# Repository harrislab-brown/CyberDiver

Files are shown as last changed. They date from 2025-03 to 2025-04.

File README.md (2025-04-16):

# CyberDiver: an untethered cyber-physical robotic impactor for water-entry experiments

<p align="center">
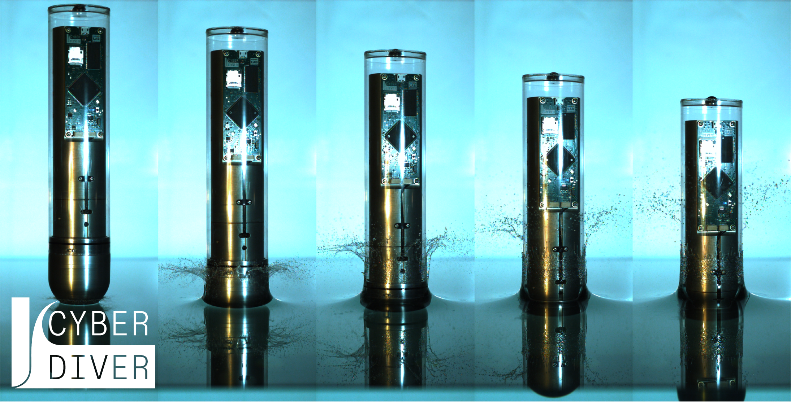
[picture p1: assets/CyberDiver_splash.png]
  
</p>

This repository provides design source files and raw data to complement the article ([https://arxiv.org/abs/2503.20702](https://arxiv.org/abs/2503.20702)). 

# License

CyberDiver is licensed under the CC BY-SA 4.0 Creative Commons license.

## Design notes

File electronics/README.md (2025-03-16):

# Electronics

This directory contains the KiCad design files, schematics, and Gerber files for the custom PCBs used in the CyberDiver. The control board and power board implement the majority of the functionality. The encoder daughterboard provides nose displacement measurements with an optical linear encoder (Celera CE300-40). The nose accelerometer board provides direct measurements of the impactor nose acceleration.

## Control board

<p align="center">
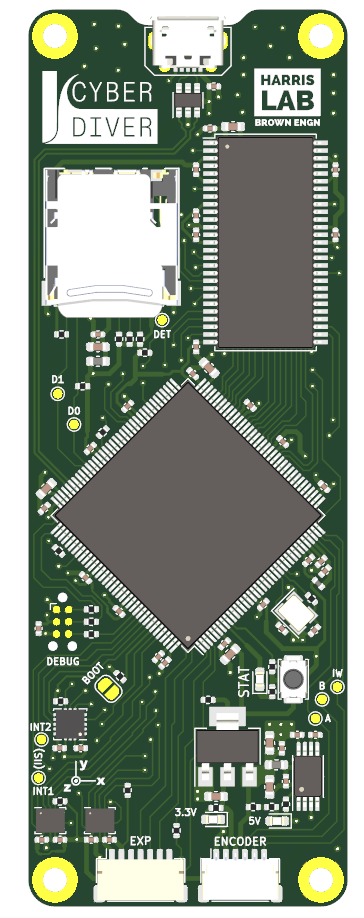
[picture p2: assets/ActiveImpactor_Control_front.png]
  
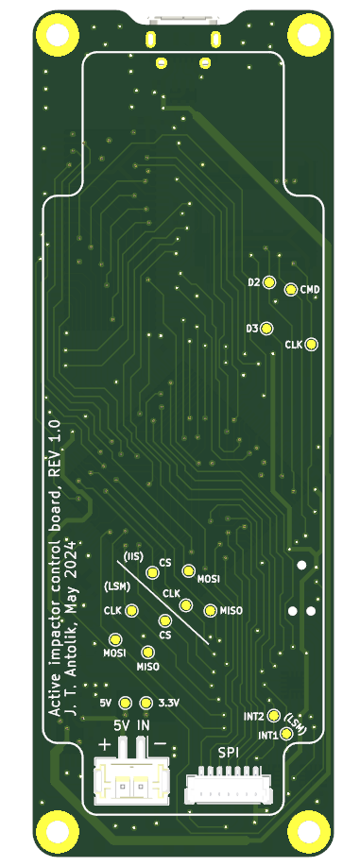
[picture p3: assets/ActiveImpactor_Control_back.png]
  
</p>

## Power board

<p align="center">
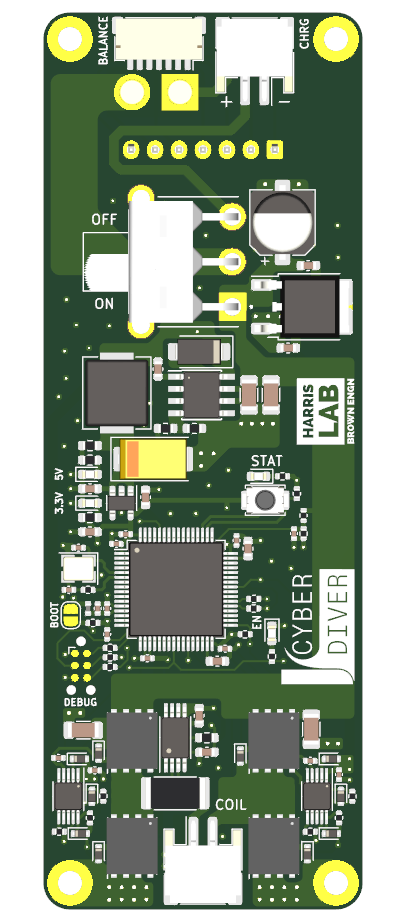
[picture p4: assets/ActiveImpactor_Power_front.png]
  
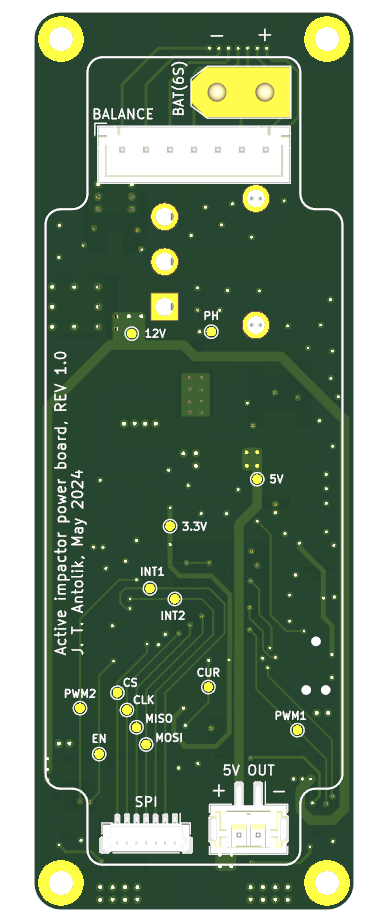
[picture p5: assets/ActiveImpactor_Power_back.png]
  
</p>

## Encoder daughter board

<p align="center">
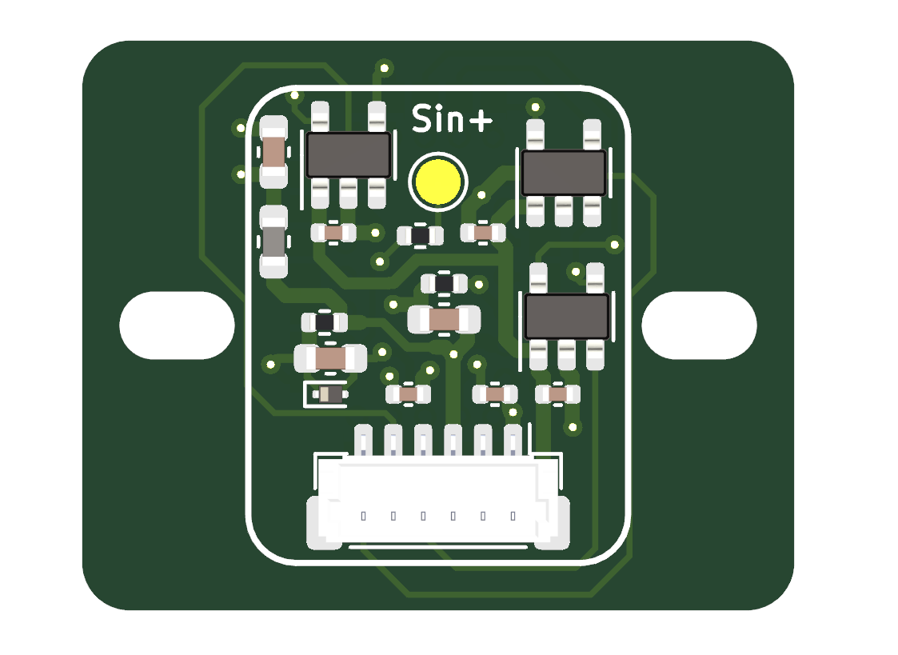
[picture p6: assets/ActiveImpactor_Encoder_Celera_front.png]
  
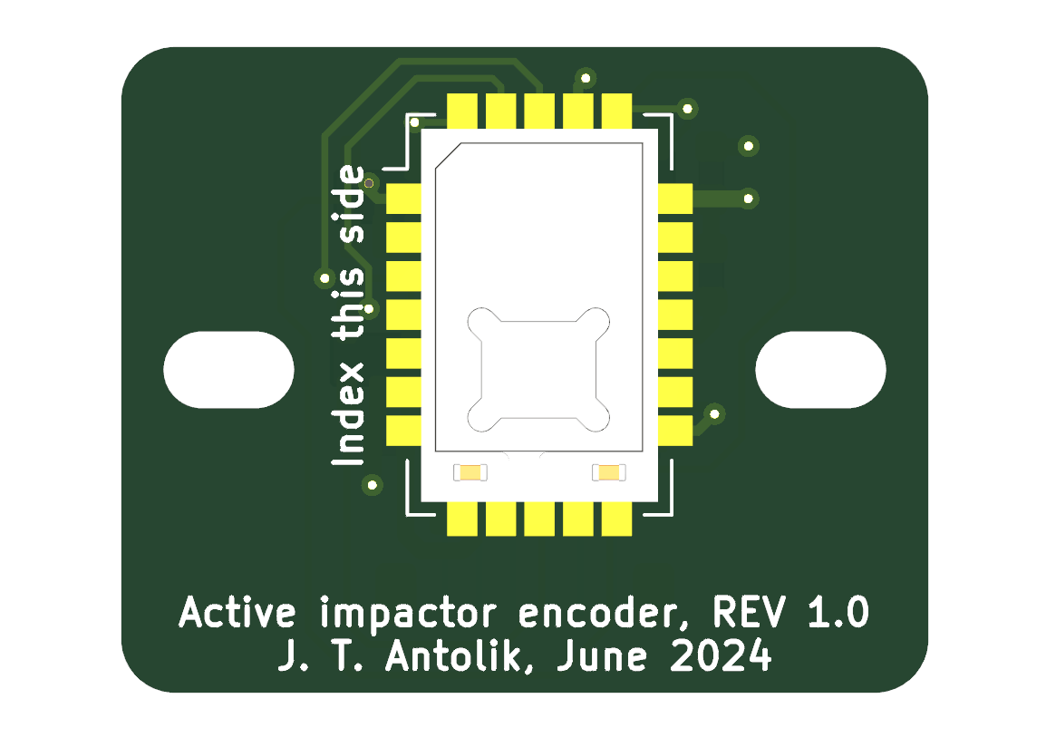
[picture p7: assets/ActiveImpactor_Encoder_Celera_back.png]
  
</p>

## Accelerometer daughter board

<p align="center">
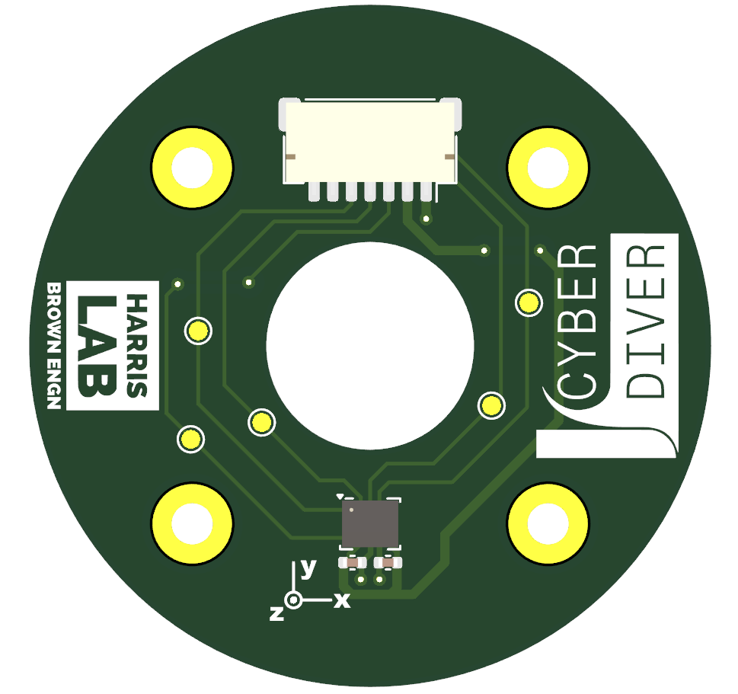
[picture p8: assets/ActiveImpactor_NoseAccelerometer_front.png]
  
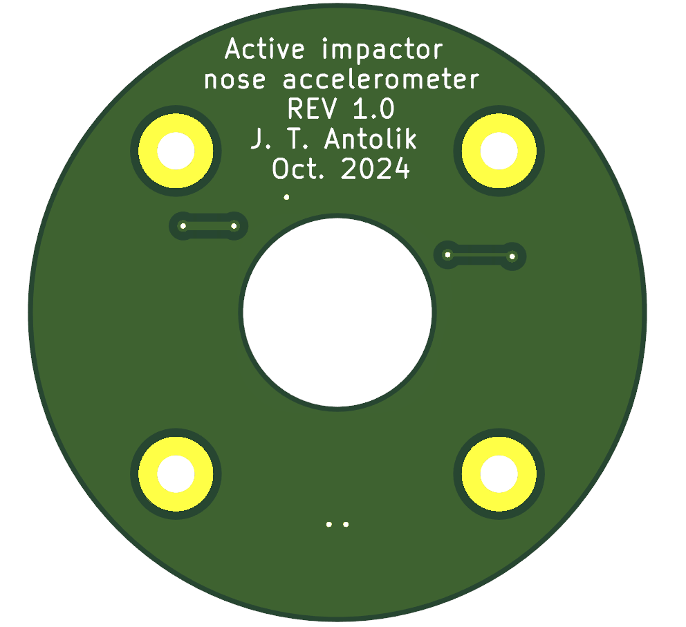
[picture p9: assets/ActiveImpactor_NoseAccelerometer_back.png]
  
</p>

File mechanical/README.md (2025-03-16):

# Mechanical

<p align="center">
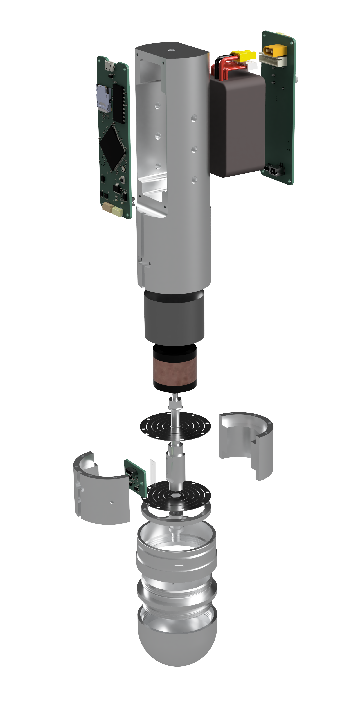
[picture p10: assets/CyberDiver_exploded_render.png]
  
</p>

This directory contains the mechanical design files for the CyberDiver including the native Autodesk Fusion 360 archive and step files. The disk flexures were laser-cut from blue-temper AISI 1075 spring steel sheet; everything else was machined from 6061 aluminum and clear anodized. The Python scripts can be executed with the Fusion 360 API to parametrically generate disk flexures with different cut profiles.

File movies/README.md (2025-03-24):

# Movies

This directory contains supplementary movies of the CyberDiver.

## Movie S1

CyberDiver entering the water at 4 m/s while behaving as a 5 N/mm undamped linear spring. The impact is filmed from above the water surface with front lighting to visualize the CyberDiver’s construction, corresponding to Figure 1(A) in the article. The playback is 100 times slower than actual speed.

## Movie S2

Demonstration of CyberDiver actuation and its position control operating mode. As the CyberDiver hangs from a bungee, a demonstration of its position control operating mode is initiated by pressing the button on the control board. The nose then moves relative to the body in a sinusoidal profile, illustrating the functionality of the actuator.

## Movie S3

Visualization of the impulse response of the cyber-physical system. An impulsive load is applied to the nose of the CyberDiver while it is suspended from a bungee and the vibrational response filmed. In the left frame, the cyber-physical system operates as a nominally undamped linear spring with 5 N/mm stiffness. In the right frame, the cyber-physical system operates as a nominally undamped linear spring with 15 N/mm stiffness. A corresponding visual difference between the amplitudes and frequencies of the vibrational responses is apparent. The playback is 25 times slower than actual speed.

## Movie S4

The CyberDiver manipulates the splash crown by performing active maneuvers during impact. The CyberDiver enters the water at 2 m/s and initiates an active maneuver at the moment of impact. Five different maneuver cases are shown where the impactor either extends or retracts the nose, resulting in amplification or attenuation of the splash formation, respectively. Movie version of Figures 6(A-E) in the article.

## Movie S5

Version of the CyberDiver splash manipulation movie with no labels. The playback in this video is 30 times slower than actual speed.

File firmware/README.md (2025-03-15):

# Firmware

This directory contains the STM32CubeIDE projects for the CyberDiver. The control board project specific header files can be found under firmware/CyberDiver_Control/Core/Inc and the implementation files under firmware/CyberDiver_Control/Core/Src. The power board project specific header files can be found under firmware/CyberDiver_Power/Core/Inc and the implementation files under firmware/CyberDiver_Power/Core/Src.

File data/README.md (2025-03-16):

# Data

<p align="center">
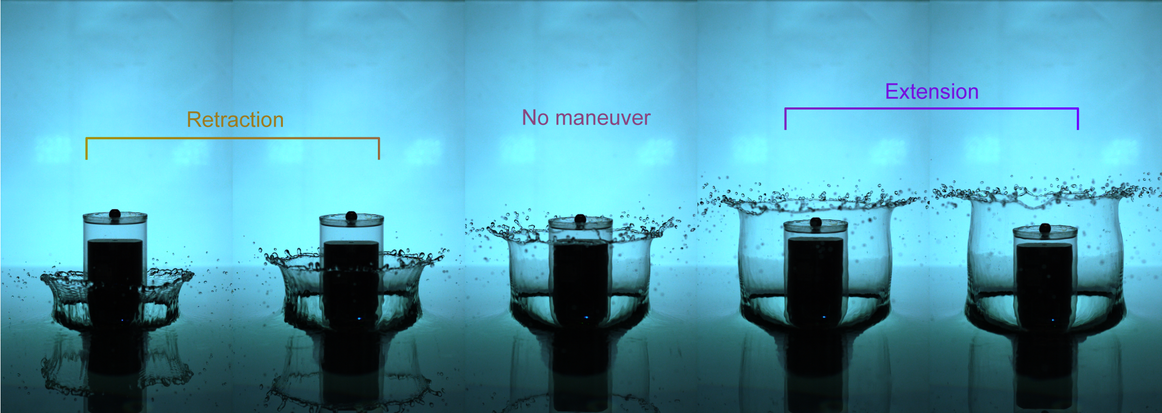
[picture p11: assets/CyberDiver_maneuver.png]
  
</p>

This directory contains the raw data files from our experiments using the CyberDiver. The CSV files contain aggregated tables of the peak acceleration corresponding to figures 3(D), 4(C), and 5(C).

## Validation

This directory contains the validation tests performed to confirm that the CyberDiver can behave as an undamped linear elastic cyber-physical system with programmable stifffess, corresponding to figures 3(A) and 3(B). The CSV files contain the quasi-static compression test results using a force test machine with displacements reported in mm and force in Newtons. The ".dat" files correspond to the dyamic ring down tests presented in figure 3(B). These are the binary data files produced by the CyberDiver that can be parsed using the provided MATLAB scripts. 

Additional force test machine results are provided for the nonlinear programmed  structural response corresponding to figure 5(A). Each of the compression test data files is labeled with either the programmed stiffness for the linear cases or the programmed force threshold in the nonlinear cases. 

Finally, ring down test data files corresponding to the damped cyber-physical structure in figure 4(A) are provided.

## Linear undamped

This directory contains the water entry experimental data files corresponding to figures 3(C) and 3(D). Each file is labeled with the linear programmed stiffness, the drop speed, and the trial number. These are the binary data files produced by the CyberDiver that can be parsed using the provided MATLAB functions in the scripts directory of this repository.

## Linear damped

This directory contains the water entry experimental data files corresponding to figures 4(B) and 4(C). Each file is labeled with the linear programmed stiffness, the drop speed, the programmed damping ratio, and the trial number. These are the binary data files produced by the CyberDiver that can be parsed using the provided MATLAB functions in the scripts directory of this repository.

## Nonlinear

This directory contains the water entry experimental data files corresponding to figures 5(B) and 5(C). Each file is labeled with the programmed force threshold, the drop speed, and the trial number. The stiffness of the linear region is 15 N/mm for all of the files in this folder. These are the binary data files produced by the CyberDiver that can be parsed using the provided MATLAB functions in the scripts directory of this repository.

## Splash manipulation

This directory contains the water entry data files corresponding to the active maneuver experiments in figure 6. Each file is labeled with the maneuver type and the trial number. These are the binary data files produced by the CyberDiver that can be parsed using the provided MATLAB functions in the scripts directory of this repository.

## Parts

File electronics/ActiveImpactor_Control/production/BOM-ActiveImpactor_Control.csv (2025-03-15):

Comment | Designator | Footprint | LCSC
100R | FB101,FB501 | L_0603_1608Metric | C1002
1k | R101,R102,R103,R104,R204 | R_0402_1005Metric | C11702
10n | C219 | C_0402_1005Metric | C15195
100n | C101,C102,C103,C105,C202,C204,C205,C207,C208,C209,C210,C211,C212,C213,C214,C215,C216,C217,C221,C301,C402,C403,C404,C405,C406,C407,C408,C501,C701,C702,C703,C704,C705,C706 | C_0402_1005Metric | C1525
12p | C203,C206 | C_0402_1005Metric | C1547
ENC | J601 | JST_SH_SM06B-SRSS-TB_1x06-1MP_P1.00mm_Horizontal | C160405
EXP | J801 | JST_SH_SM07B-SRSS-TB_1x07-1MP_P1.00mm_Horizontal | C160406
10u | C104,C201,C401,C502 | C_0603_1608Metric | C19702
DM3CS-SF | J501 | DM3CS-SF_HIR | C202111
BUTTON | SW201 | SW_Push_SPST_NO_Alps_SKRK | C202388
2u2 | C220,C222 | C_0603_1608Metric | C23630
22 | R205,R206,R207,R401,R502,R802 | R_0402_1005Metric | C25092
47 | R202 | R_0402_1005Metric | C25118
10k | R201,R203 | R_0402_1005Metric | C25744
47k | R501,R503,R504,R505,R506,R507,R701,R702,R703,R801 | R_0402_1005Metric | C25792
39n | L201 | L_0402_1005Metric | C26443
22u | C106,C107 | C_0603_1608Metric | C2762594
USBLC6-2SC6 | U301 | SOT-23-6 | C2827654
ADXL373 | U702 | Analog_LGA-16_3.25x3mm_P0.5mm_LayoutBorder3x5y | C3216386
USB_B_Micro | J301 | MicroXNJ | C404969
1u | C218 | C_0402_1005Metric | C52923
AMS1117-3.3 | U102 | SOT-223-3_TabPin2 | C6186
W9812G6KH-6 | U401 | TSOP-II-54_22.2x10.16mm_P0.8mm | C62379
TPS2115APWR | U101 | TSSOP-8_4.4x3mm_P0.65mm | C70287
24MHz | Y201 | Crystal_SMD_3225-4Pin_3.2x2.5mm | C70590
IIS3DWBTR | U703 | LGA-14_3x2.5mm_P0.5mm_LayoutBorder3x4y | C717702
STM32H723ZGTx | U201 | LQFP-144_20x20mm_P0.5mm | C730146
STAT | D201 | LED_0603_1608Metric | C84266
LED_5V | D101,D102 | LED_0603_1608Metric | C965805
LSM6DS3TR-C | U701 | LGA-14_3x2.5mm_P0.5mm_LayoutBorder3x4y | C967633

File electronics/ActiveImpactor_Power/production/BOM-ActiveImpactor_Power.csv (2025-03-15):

Comment | Designator | Footprint | LCSC
TLV70033_SOT23-5 | U102 | SOT-23-5 | C11337
1k | R109,R111,R201 | R_0402_1005Metric | C11702
100u | C101 | CP_Elec_6.3x5.8 | C128464
INA240A2PWR | U303 | TSSOP-8_4.4x3mm_P0.65mm | C129949
16MHz | Y201 | Crystal_SMD_3225-4Pin_3.2x2.5mm | C13738
7k5 | R108 | R_0402_1005Metric | C137934
100n | C303,C305 | C_0603_1608Metric | C14663
10n | C106,C210 | C_0402_1005Metric | C15195
100n | C202,C205,C206,C207,C208,C212 | C_0402_1005Metric | C1525
12p | C211,C213 | C_0402_1005Metric | C1547
STM32F405RGT6 | U201 | LQFP-64_10x10mm_P0.5mm | C15742
Balance | J104 | JST_SH_SM07B-SRSS-TB_1x07-1MP_P1.00mm_Horizontal | C160406
L7812 | U301 | TO-252-2 | C16424
1u | C306,C307 | C_1206_3216Metric | C1848
330n | C301 | C_0603_1608Metric | C188679
4u7 | C108,C109 | C_0603_1608Metric | C19666
10u | C201 | C_0603_1608Metric | C19702
BUTTON | SW201 | SW_Push_SPST_NO_Alps_SKRK | C202388
1k | R106,R107,R110,R112 | R_0603_1608Metric | C21190
LED_EN | D103 | LED_0603_1608Metric | C2286
3.24k | R105 | R_0603_1608Metric | C22994
2u2 | C203,C204 | C_0603_1608Metric | C23630
220u | C105 | CP_EIA-7343-40_Kemet-Y | C242173
10 | R303,R304,R305,R306 | R_0402_1005Metric | C25077
22 | R102,R103,R205,R206,R207 | R_0402_1005Metric | C25092
47 | R204 | R_0402_1005Metric | C25118
10k | R202,R203 | R_0402_1005Metric | C25744
20k | R301,R307 | R_0402_1005Metric | C25765
47k | R101 | R_0402_1005Metric | C25792
10k | R104 | R_0603_1608Metric | C25804
39n | L201 | L_0402_1005Metric | C26443
Charge | J105,J301 | JST_PH_S2B-PH-SM4-TB_1x02-1MP_P2.00mm_Horizontal | C295747
4.7u | C102,C103 | C_1206_3216Metric | C29823
6m | R302 | R_2512_6332Metric | C2985709
22u | L101 | L_Sunlord_MWSA0603S | C408453
470n | C302,C309 | C_0402_1005Metric | C437527
SIR182DP | Q301,Q302,Q303,Q304 | PowerPAK_SO-8_Single | C467943
1u | C209 | C_0402_1005Metric | C52923
4.7n | C107 | C_0603_1608Metric | C53987
1N5819 | D301,D304,D305,D306,D307,D310 | D_SOD-523 | C5451630
10n | C104 | C_0603_1608Metric | C57112
B340 | D101 | D_SMA | C64982
1N4148WT | D302,D303,D308,D309 | D_SOD-523 | C727112
STAT | D201 | LED_0603_1608Metric | C84266
47n | C304,C308 | C_0402_1005Metric | C880605
LM5106 | U302,U304 | VSSOP-10_3x3mm_P0.5mm | C91879
LED_5V | D102,D104 | LED_0603_1608Metric | C965805
TPS5430DDA | U101 | TI_SO-PowerPAD-8_ThermalVias | C9864

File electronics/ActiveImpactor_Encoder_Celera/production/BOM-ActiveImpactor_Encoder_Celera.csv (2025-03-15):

Comment | Designator | Footprint | LCSC
1k | R102 | R_0402_1005Metric | C11702
ESD9X3.3ST5G | D101 | D_SOD-923 | C130456
MAX3280EAUK | U102,U103,U104 | SOT-23-5 | C131126
100n | C101,C102,C106,C107,C108 | C_0402_1005Metric | C1525
1u | C103,C104,C105 | C_0603_1608Metric | C15849
Conn_01x06 | J101 | JST_SH_BM06B-SRSS-TB_1x06-1MP_P1.00mm_Vertical | C160392
600Ω @ 100 MHz | L101 | L_0603_1608Metric | C19330
120 | R101 | R_0402_1005Metric | C25079
7.15k | R103 | R_0402_1005Metric | C270586

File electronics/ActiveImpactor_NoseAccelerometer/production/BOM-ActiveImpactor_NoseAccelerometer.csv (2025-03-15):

Comment | Designator | Footprint | LCSC
100n | C101,C102 | C_0402_1005Metric | C1525
EXP | J101 | JST_SH_SM07B-SRSS-TB_1x07-1MP_P1.00mm_Horizontal | C160406
LSM6DS3TR-C | U101 | LGA-14_3x2.5mm_P0.5mm_LayoutBorder3x4y | C1864162

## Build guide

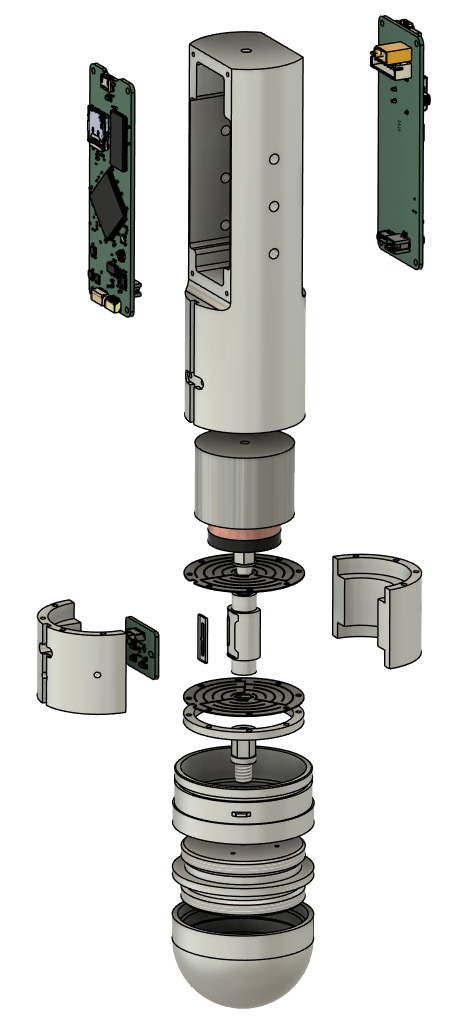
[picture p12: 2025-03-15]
assets/CyberDiver_exploded_assembly.png

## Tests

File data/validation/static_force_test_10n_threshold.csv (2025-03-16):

Trial 1_x | Trial 1_y | Trial 2_x | Trial 2_y | Trial 3_x | Trial 3_y
-0. | -0.0002942002 | -0. | -0.0025065859 | -0. | -0.0015180731
-0. | 0.0063194207 | -0. | 0.0019181854 | -0. | -0.0028360901
-0. | 0.0063194207 | -0. | 0.0019181854 | -0. | 0.0011650329
-0. | 0.0020594015 | -0. | 0.0006237045 | -0. | -0.0016122172
-0. | -0.0019887935 | -0. | 0.0009767447 | -0. | -0.0016122172
-0. | -0.0019887935 | -0.034375 | 0.0025065859 | -0. | 0.0006472405
-0. | 0.0016828252 | -0.034375 | 0.0025065859 | -0.0375 | 0.0035421706
-0.040625 | 0.0009767447 | -0.034375 | 0.0039893549 | -0.0375 | 0.0020358655
-0.040625 | -0.0009532087 | -0.034375 | -0.0007884566 | -0.0375 | -0.0020829375
-0.040625 | 0.0001059121 | -0.034375 | 0.0007178485 | -0.0375 | -0.0020829375
-0.040625 | 0.0001059121 | -0.034375 | -0.0004824884 | -0.0375 | -0.0002235922
-0.040625 | 0.0020829375 | -0.084375 | -0.0036127787 | -0.0375 | 0.0038010668
-0.040625 | 0.0014710011 | -0.084375 | -0.0036127787 | -0.0875 | -0.0015651452
-0.090625 | -0.0028360901 | -0.084375 | -0.0024595138 | -0.0875 | -0.001306249
-0.090625 | 0.0064371008 | -0.084375 | -0.0020829375 | -0.0875 | -0.001306249
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

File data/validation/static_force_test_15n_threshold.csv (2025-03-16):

Trial 1_x | Trial 1_y | Trial 2_x | Trial 2_y | Trial 3_x | Trial 3_y
-0. | -0.0023182977 | -0. | -0.0077080457 | -0. | 0.0003648083
-0. | -0.0021770816 | -0. | -0.0010944248 | -0. | 0.004012891
-0. | -0.0008355286 | -0.00625 | -0.0010944248 | -0. | 0.0016357532
-0. | -0.0008355286 | -0.00625 | -0.0006707765 | -0. | 0.0016357532
-0. | 0.0056839482 | -0.00625 | 0.0005530964 | -0. | 0.0007178485
-0. | -0.0010473528 | -0.00625 | 0.0016828252 | -0.028125 | 0.002694874
-0. | 0.0019181854 | -0.00625 | 0.0016828252 | -0.028125 | 0.0020358655
-0.05 | -0.0000353040 | -0.00625 | -0.0018946494 | -0.028125 | 0.002694874
-0.05 | -0.0000353040 | -0.05625 | -0.0008355286 | -0.028125 | 0.002694874
-0.05 | -0.0008590646 | -0.05625 | 0.0000117680 | -0.028125 | 0.0004824884
-0.05 | -0.0002471282 | -0.05625 | -0.0023889058 | -0.028125 | -0.0005766324
-0.05 | -0.0022241536 | -0.05625 | -0.0032362024 | -0.078125 | -0.0014239291
-0.05 | -0.0032126664 | -0.05625 | -0.0032362024 | -0.078125 | 0.0024124418
-0.1 | -0.0032126664 | -0.05625 | -0.0011650329 | -0.078125 | 0.0024124418
-0.1 | -0.0054250520 | -0.10625 | -0.0006472405 | -0.078125 | 0.0021535456
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

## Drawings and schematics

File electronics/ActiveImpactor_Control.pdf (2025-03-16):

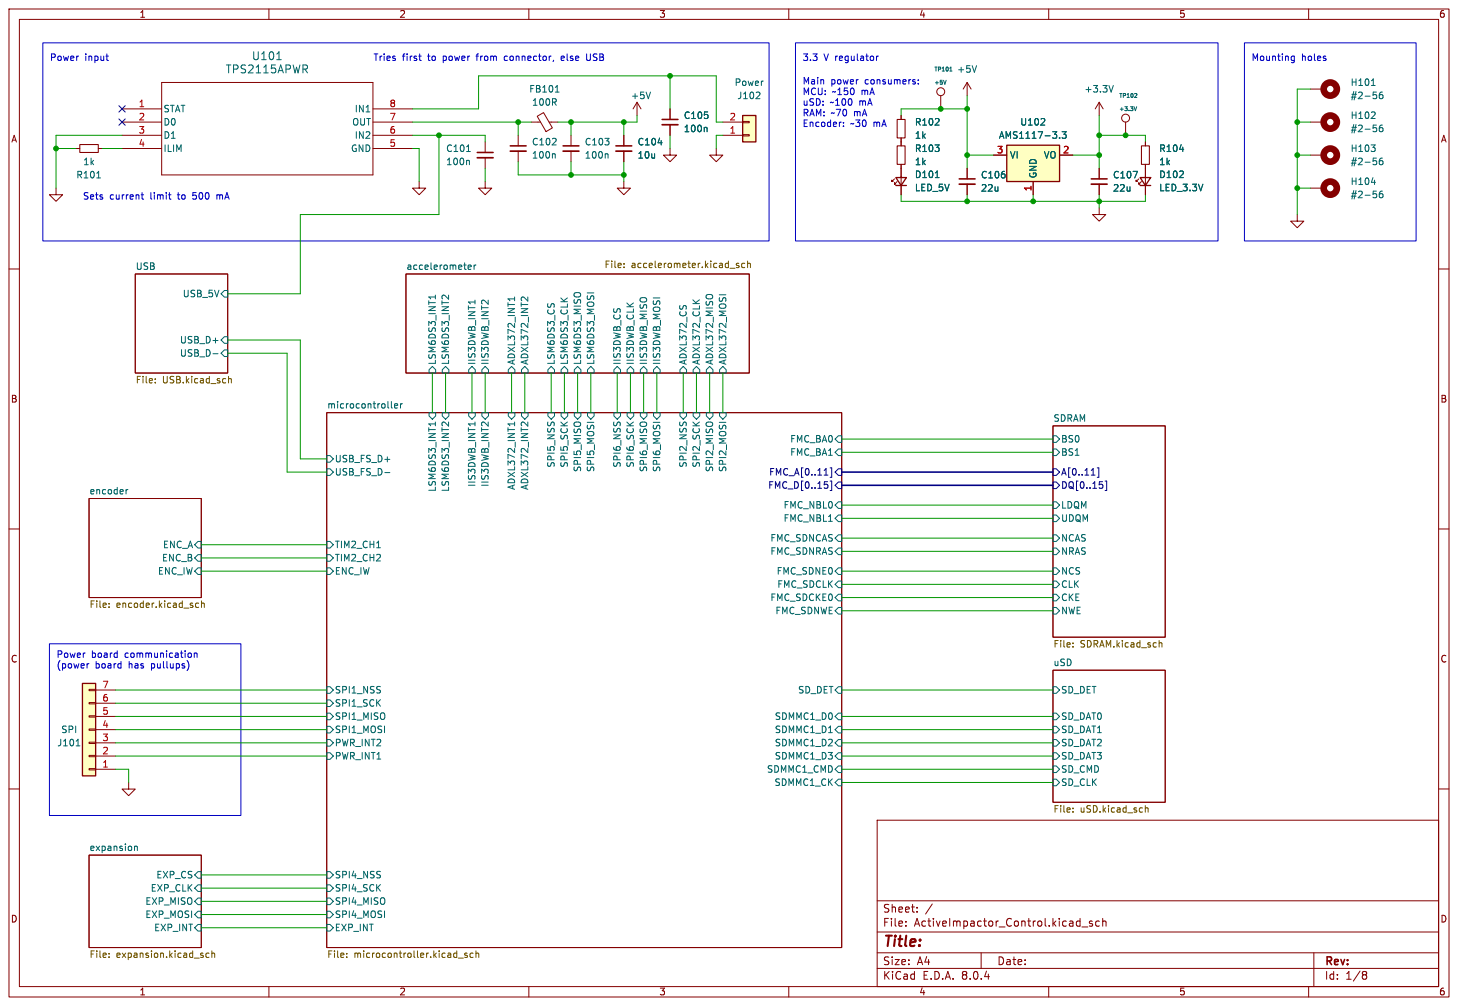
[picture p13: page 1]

Mounting holes Main power consumers: MCU: ~150 mA

uSD: ~100 mA RAM: ~70 mA

100n Power board communication
LED_3.3V R101
Sets current limit to 500 mA

SDRAM
BS1 BS0 CLK NCS
DQ[0..15] CKE NCAS UDQM
LDQM

(power board has pullups)

Id: 1/8 Title: File: ActiveImpactor_Control.kicad_sch Sheet: /

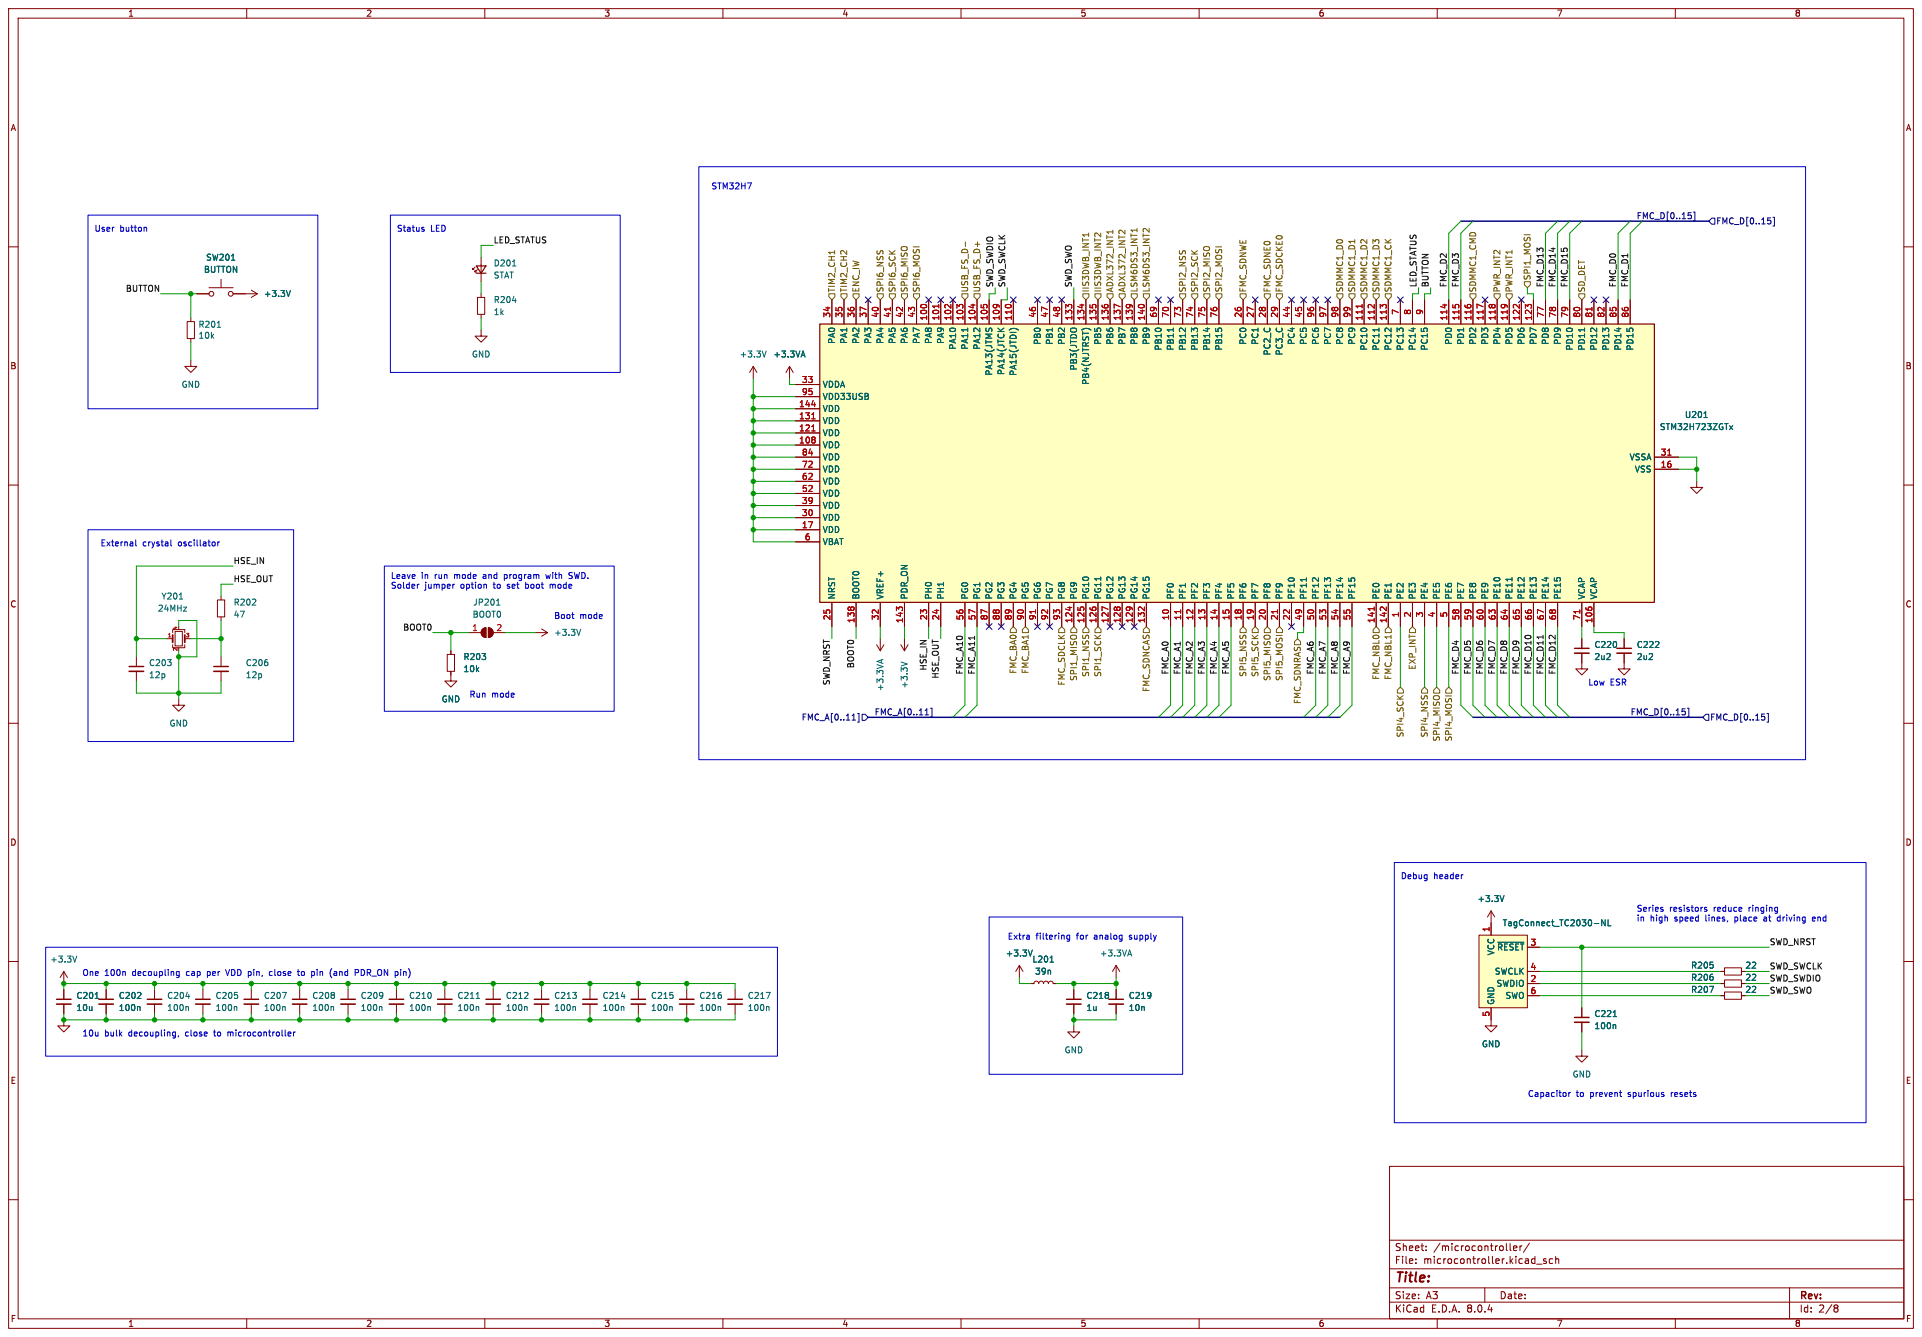
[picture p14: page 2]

Leave in run mode and program with SWD. Solder jumper option to set boot mode User button

in high speed lines, place at driving end

1 SWDIO 2 ~{RESET}3 SWCLK 4 GND

Id: 2/8 Title: File: microcontroller.kicad_sch Sheet: /microcontroller/ +3.3V

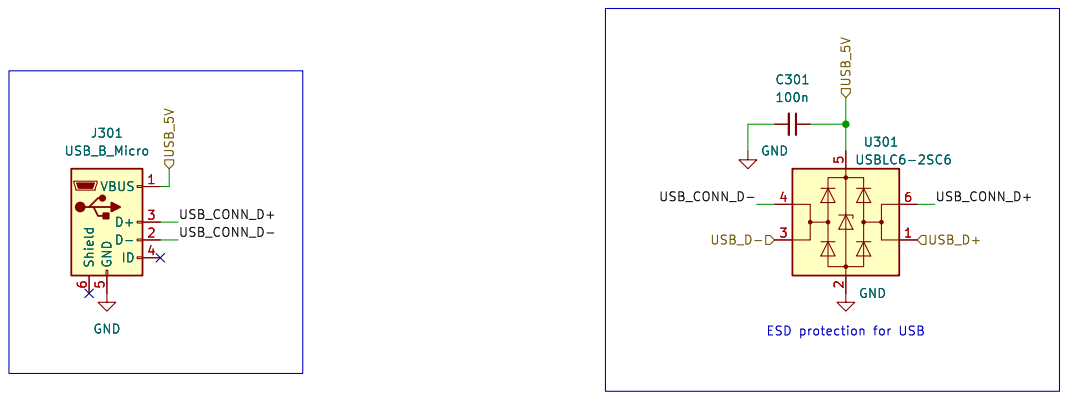
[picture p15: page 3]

Id: 3/8 Title: File: USB.kicad_sch Sheet: /USB/ GND

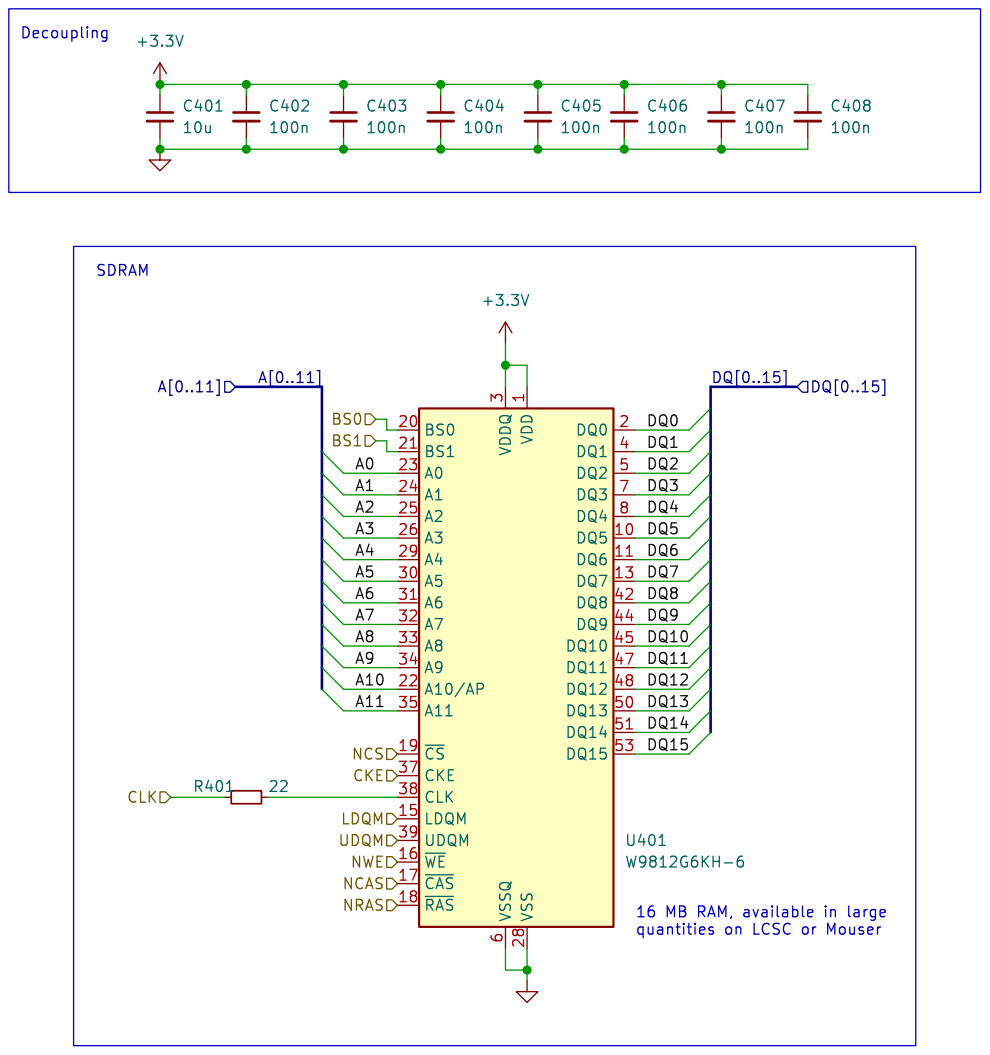
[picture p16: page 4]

Id: 4/8 Title: File: SDRAM.kicad_sch Sheet: /SDRAM/

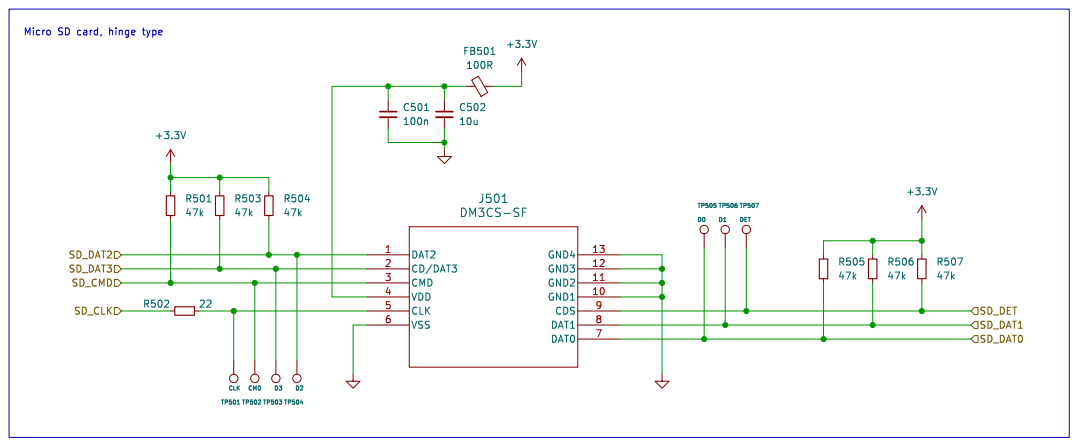
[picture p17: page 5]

SD_DET SD_DAT0 SD_DAT1 SD_CLK Micro SD card, hinge type

Id: 5/8 Title: File: uSD.kicad_sch Sheet: /uSD/

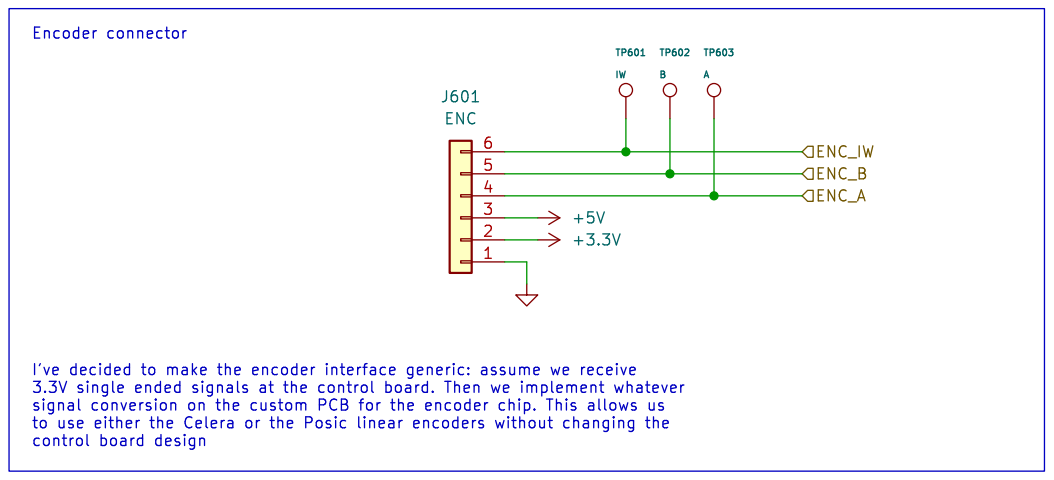
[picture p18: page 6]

Id: 6/8 Title: File: encoder.kicad_sch Sheet: /encoder/

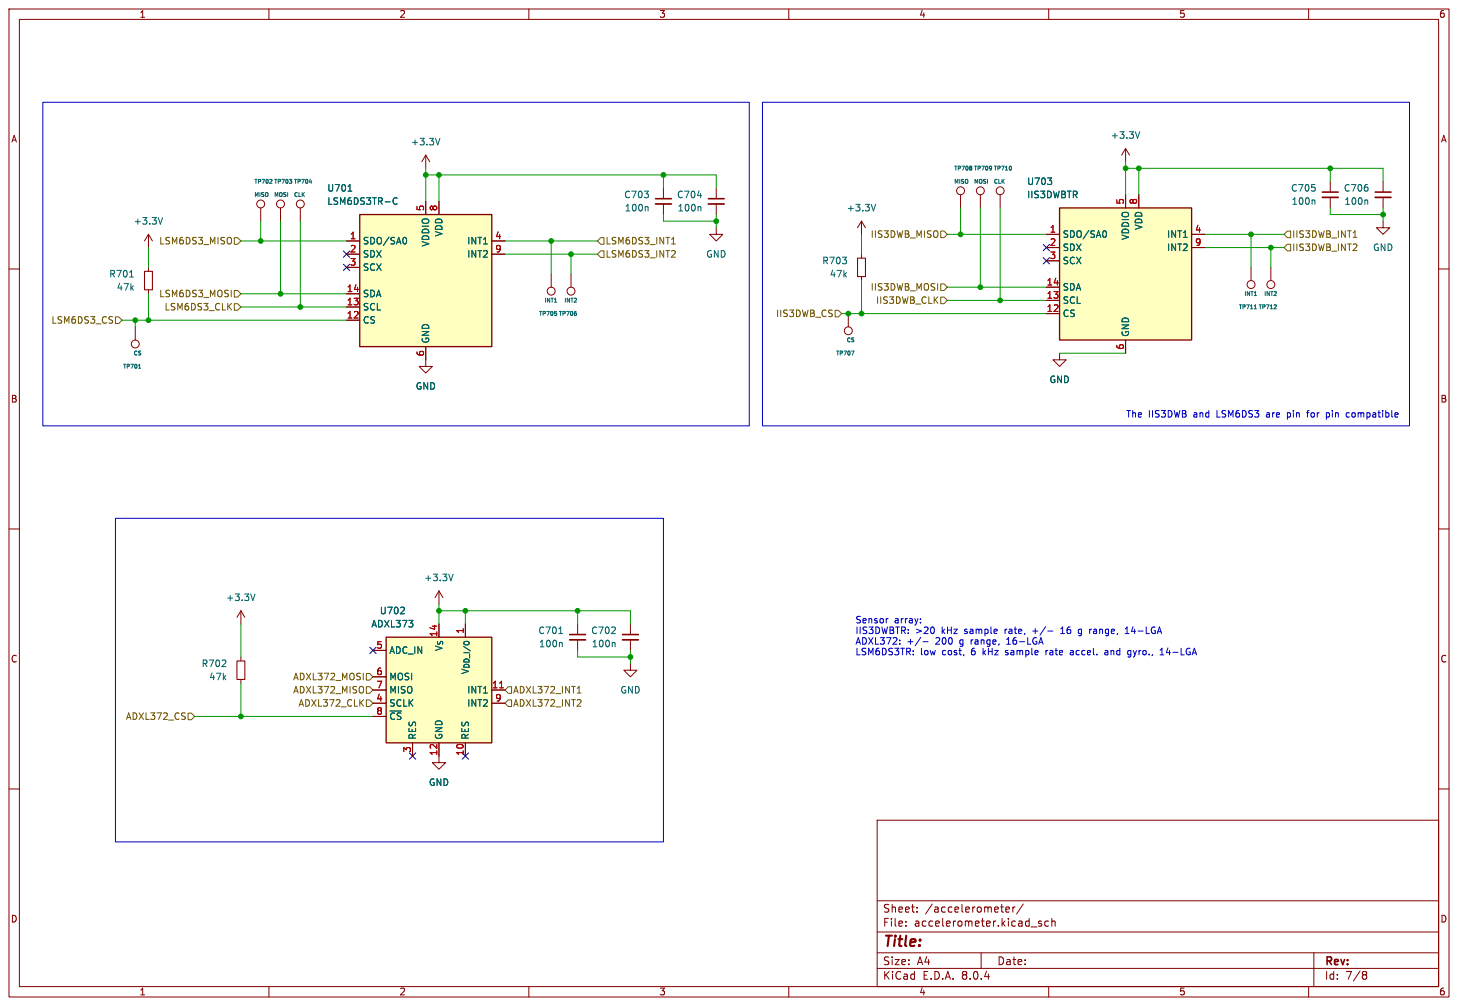
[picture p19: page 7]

The IIS3DWB and LSM6DS3 are pin for pin compatible Sensor array:

LSM6DS3TR: low cost, 6 kHz sample rate accel. and gyro., 14-LGA

3 SCLK 4 ADC_IN 5 MOSI 6 MISO 7 ~{CS} 8

Id: 7/8 Title: File: accelerometer.kicad_sch Sheet: /accelerometer/

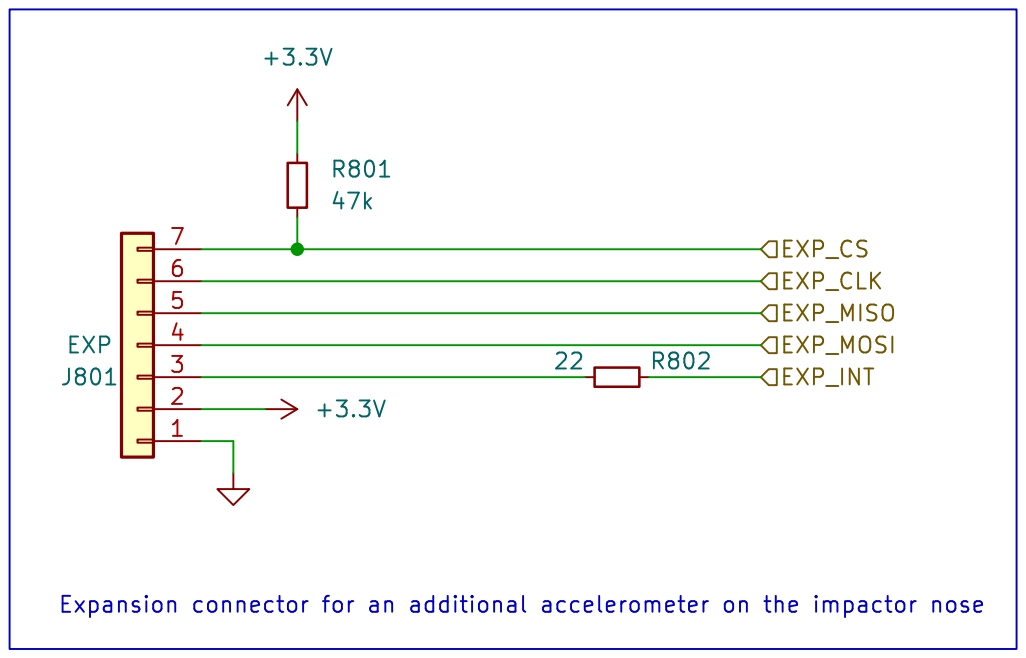
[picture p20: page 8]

Id: 8/8 Title: File: expansion.kicad_sch Sheet: /expansion/

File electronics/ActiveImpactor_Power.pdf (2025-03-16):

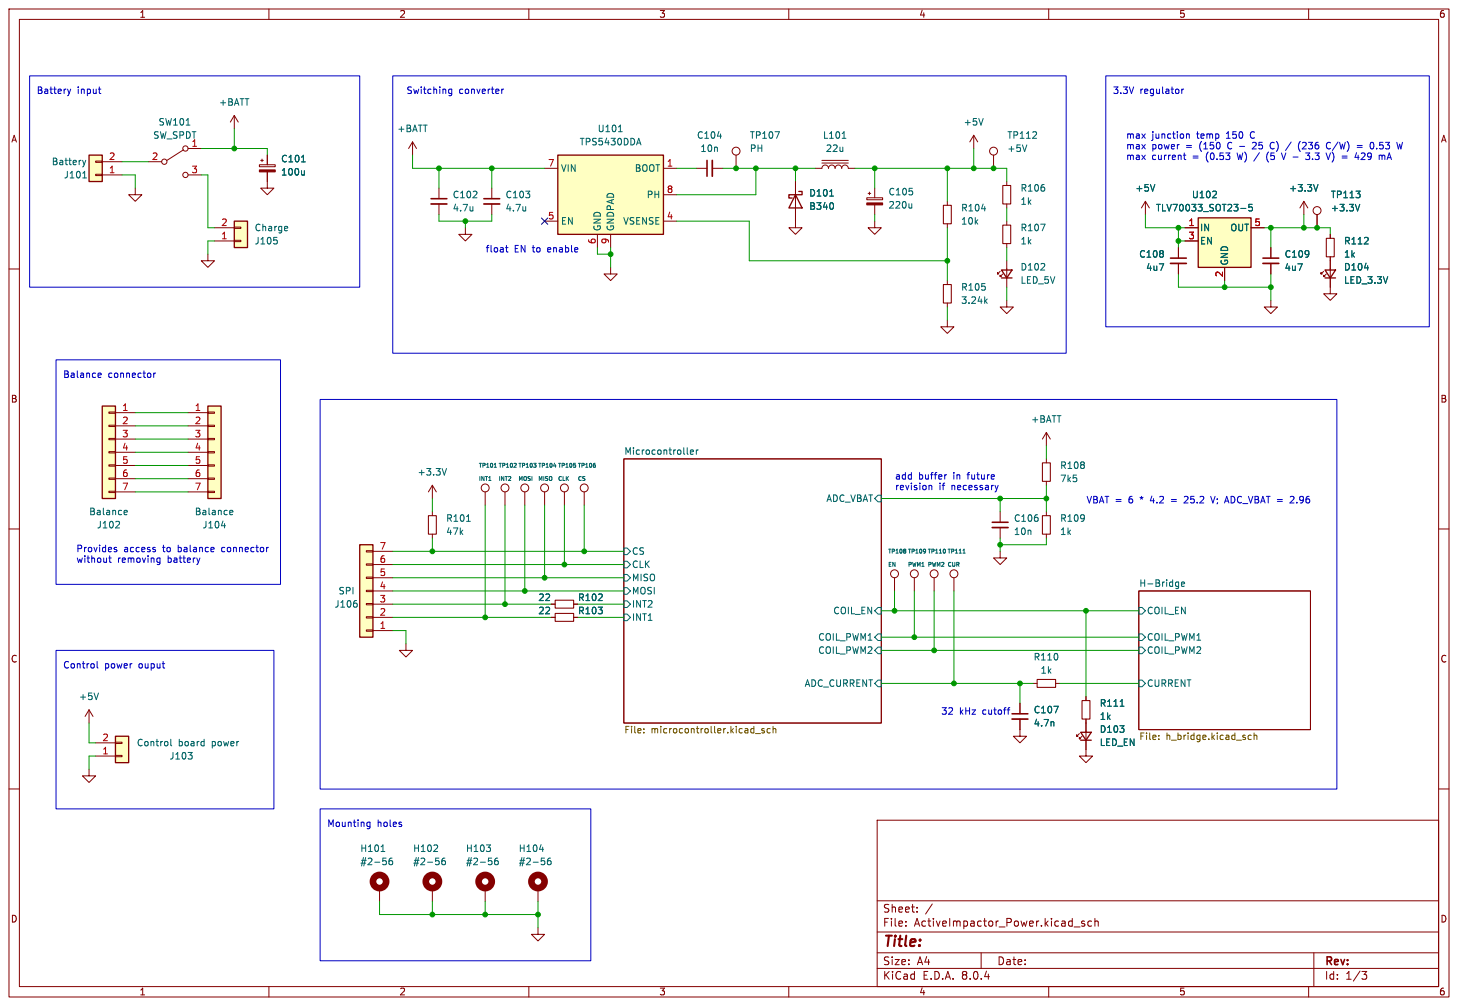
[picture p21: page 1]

add buffer in future

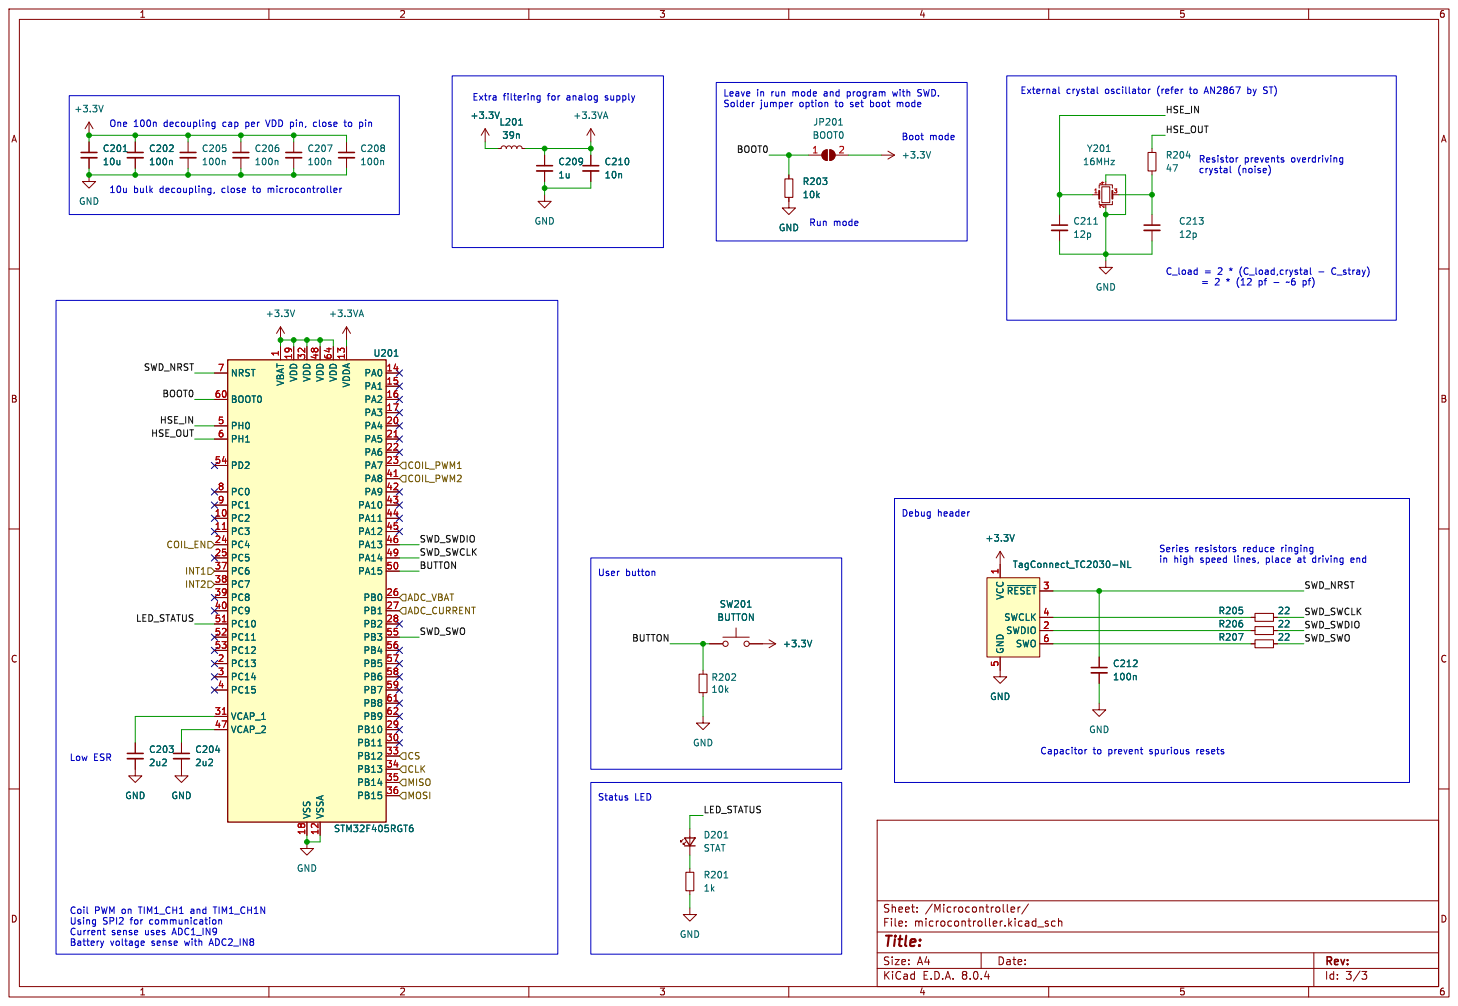
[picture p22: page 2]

Leave in run mode and program with SWD. Solder jumper option to set boot mode U201 STM32F405RGT6 VBAT

Boot mode Run mode Status LED

1 PC2 10 PC3 11 VSSA 12 VDDA 13 PA0 14 PA1 15 PA2 16 PA3 17 VSS 18 VDD 19 PC13 2 PA4 20 PA5 21 PA6 22 PA7 23 PC4 24 PC5 25 PB0 26 PB1 27 PB2 28 PB10 29 PC14 3 PB11 30 VCAP_1 31 VDD 32 PB12 33 PB13 34 PB14 35 PB15 36 PC6 37 PC7 38 PC8 39 PC15 4 PC9 40 PA8 41 PA9 42 PA10 43 PA11 44 PA12 45 PA13 46 VCAP_2 47 VDD 48 PA14 49 PH0 5 PA15 50 PC10 51 PC11 52 PC12 53 PD2 54 PB3 55 PB4 56 PB5 57 PB6 58 PB7 59 PH1 6 BOOT0 60 PB8 61 PB9 62 VDD 64 NRST 7 PC0 8 PC1 9 C204

1 PC2 10 PC3 11 VSSA 12 VDDA 13 PA0 14 PA1 15 PA2 16 PA3 17 VSS 18 VDD 19 PC13 2 PA4 20 PA5 21 PA6 22 PA7 23 PC4 24 PC5 25 PB0 26 PB1 27 PB2 28 PB10 29 PC14 3 PB11 30 VCAP_1 31 VDD 32 PB12 33 PB13 34 PB14 35 PB15 36 PC6 37 PC7 38 PC8 39 PC15 4 PC9 40 PA8 41 PA9 42 PA10 43 PA11 44 PA12 45 PA13 46 VCAP_2 47 VDD 48 PA14 49 PH0 5 PA15 50 PC10 51 PC11 52 PC12 53 PD2 54 PB3 55 PB4 56 PB5 57 PB6 58 PB7 59 PH1 6 BOOT0 60 PB8 61 PB9 62 VDD 64 NRST 7 PC0 8 PC1 9 U201 STM32F405RGT6

1 SWDIO 2 ~{RESET}3 SWCLK 4 GND

Id: 3/3 Title: File: microcontroller.kicad_sch Sheet: /Microcontroller/

Using SPI2 for communication Current sense uses ADC1_IN9 Battery voltage sense with ADC2_IN8

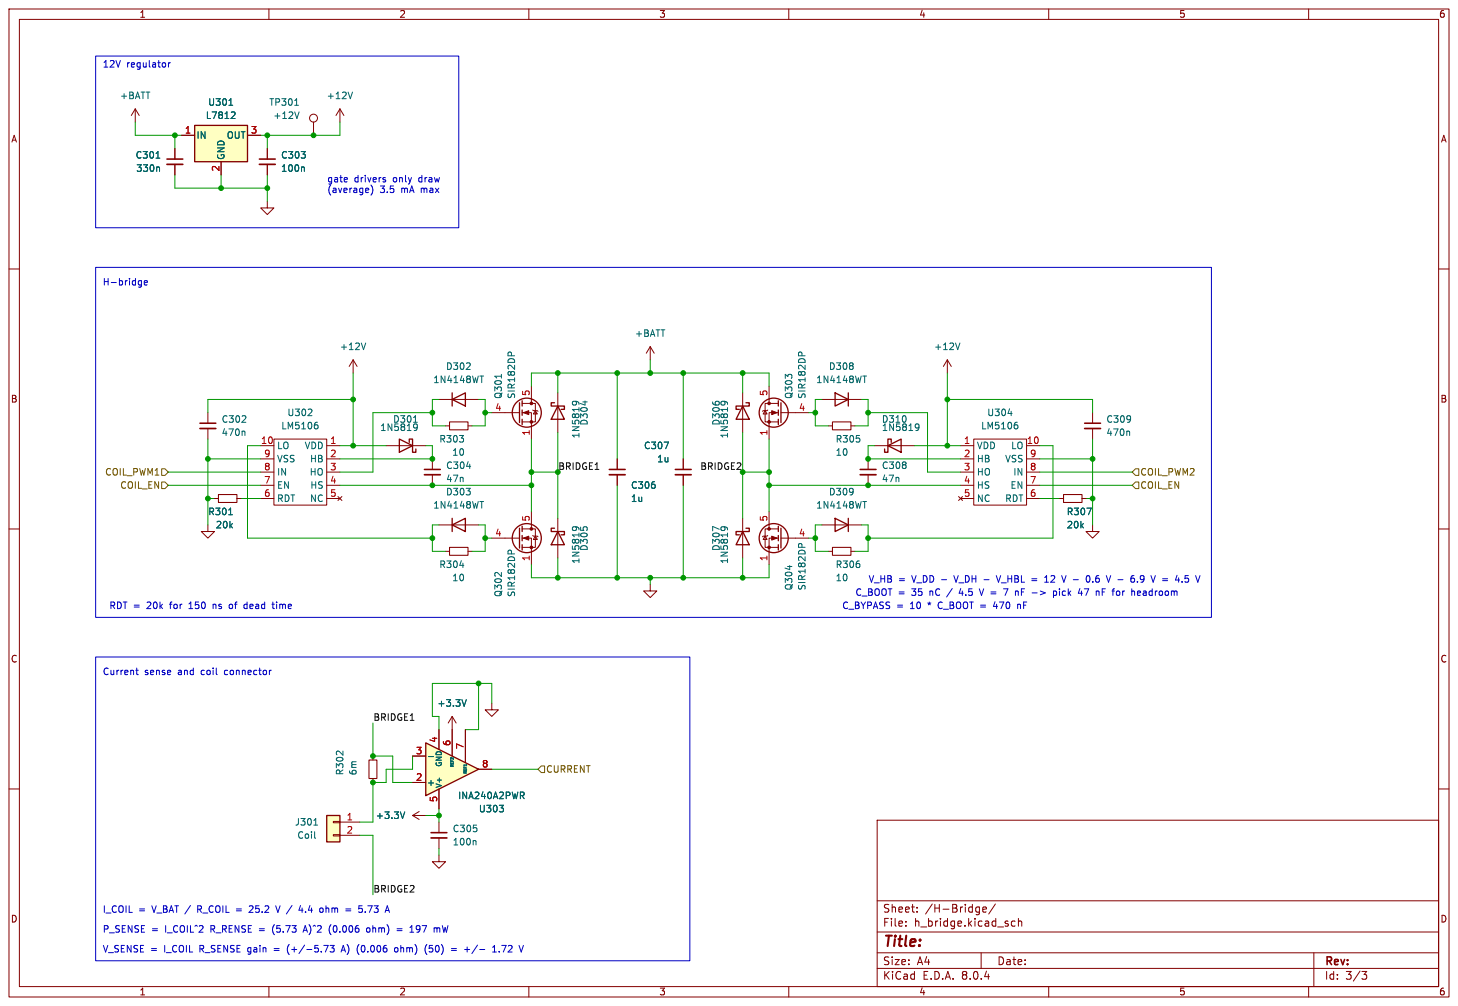
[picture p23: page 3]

gate drivers only draw

Id: 3/3 Title: File: h_bridge.kicad_sch Sheet: /H-Bridge/ D309

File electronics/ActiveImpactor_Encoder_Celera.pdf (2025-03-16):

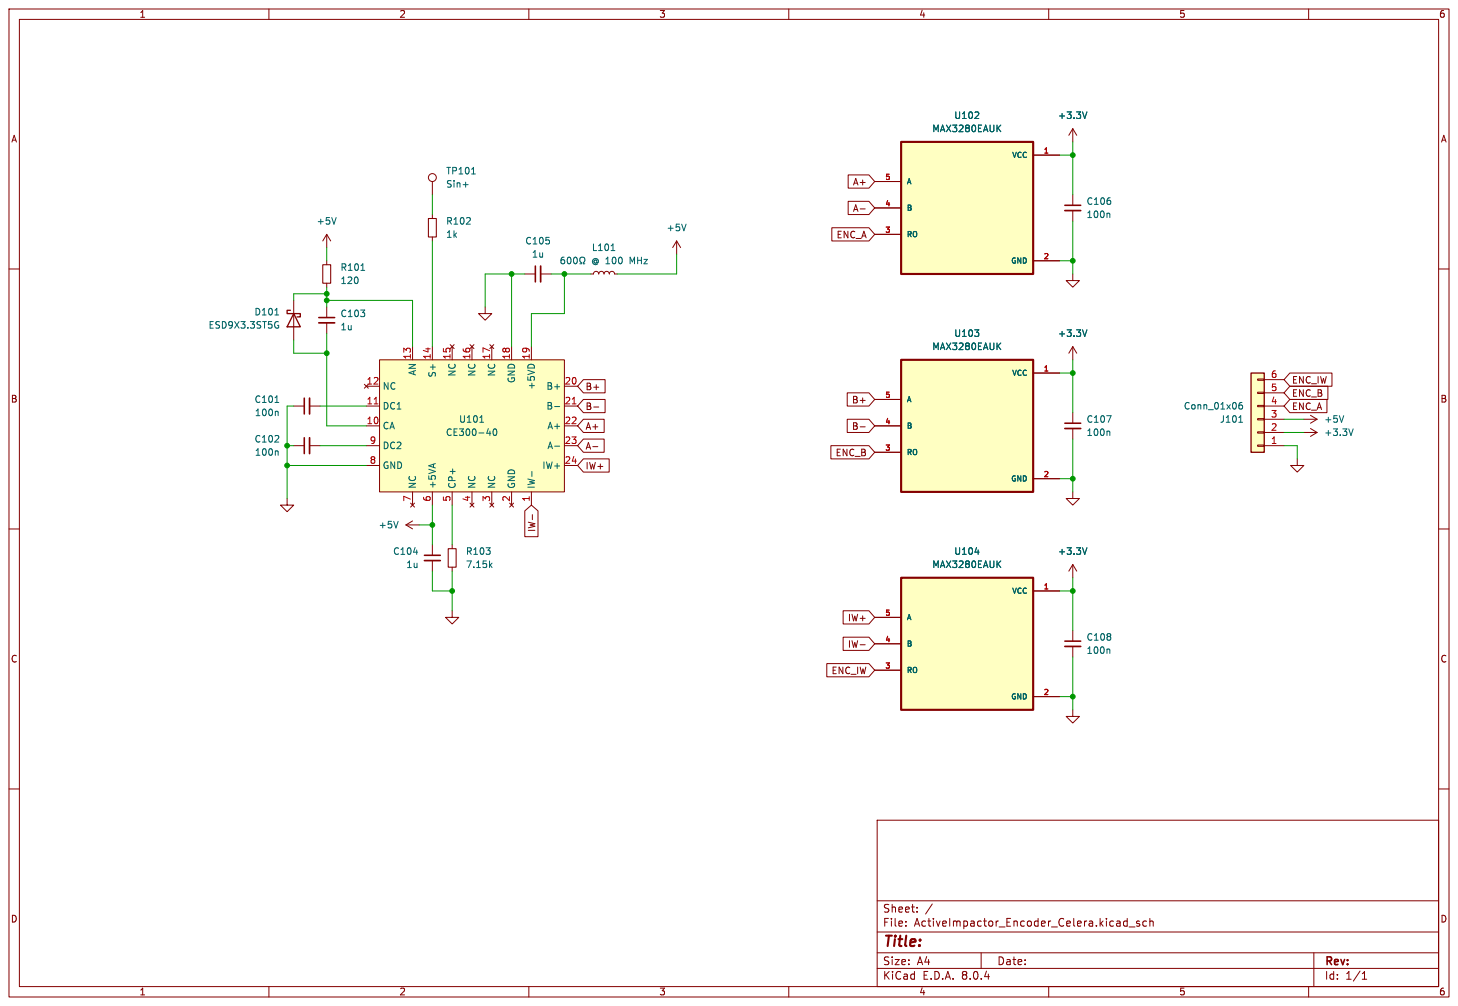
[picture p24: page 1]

Id: 1/1 Title: File: ActiveImpactor_Encoder_Celera.kicad_sch Sheet: / R103

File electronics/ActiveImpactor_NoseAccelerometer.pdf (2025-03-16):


Id: 1/1 Title: File: ActiveImpactor_NoseAccelerometer.kicad_sch Sheet: /







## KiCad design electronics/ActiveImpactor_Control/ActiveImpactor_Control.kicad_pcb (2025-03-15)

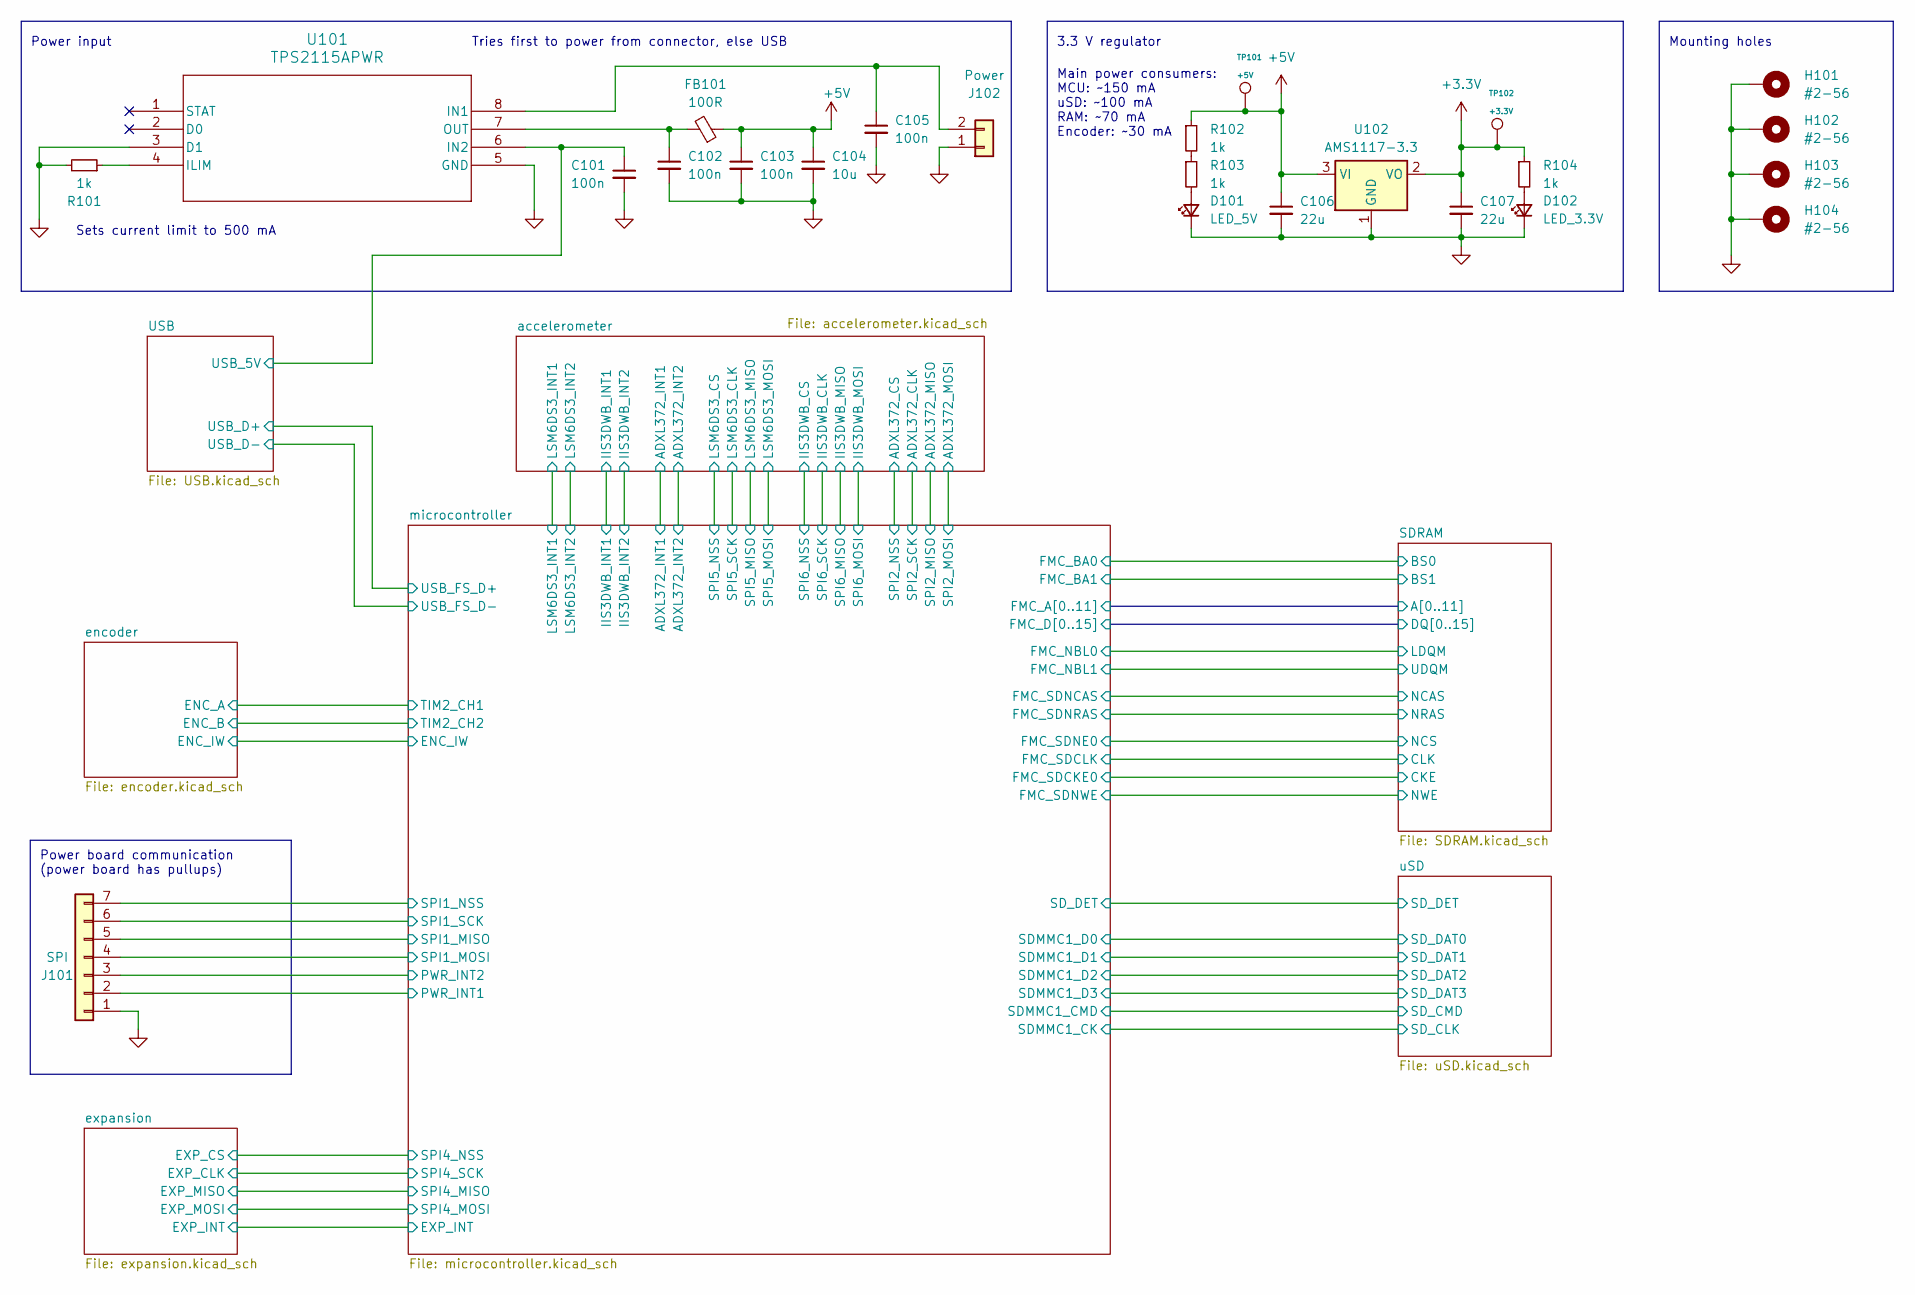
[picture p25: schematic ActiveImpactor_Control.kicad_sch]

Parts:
C101, C102, C103, C105: 100n; C_0402_1005Metric; LCSC C1525
C104: 10u; C_0603_1608Metric; LCSC C19702
C106, C107: 22u; C_0603_1608Metric; LCSC C2762594
D101: LED_5V; LED_0603_1608Metric; LCSC C965805
D102: LED_3.3V; LED_0603_1608Metric; LCSC C965805
FB101: 100R; L_0603_1608Metric; LCSC C1002
H101, H102, H103, H104: #2-56; MountingHole_2.5mm_Pad
J101: SPI; JST_SH_BM07B-SRSS-TB_1x07-1MP_P1.00mm_Vertical; Digikey 455-BM07B-SRSS-TBCT-ND
J102: Power; JST_PH_B2B-PH-SM4-TB_1x02-1MP_P2.00mm_Vertical; Digikey 455-B2B-PH-SM4-TBCT-ND
R101, R102, R103, R104: 1k; R_0402_1005Metric; LCSC C11702
TP101: +5V; TestPoint_Pad_D1.0mm
TP102: +3.3V; TestPoint_Pad_D1.0mm
U101: TPS2115APWR; TSSOP-8_4.4x3mm_P0.65mm; LCSC C70287
U102: AMS1117-3.3; SOT-223-3_TabPin2; LCSC C6186

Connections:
+3.3V: C107.1, R104.1, TP102.1, U102.2 (VO); also elsewhere on the board
+5V: C103.1, C104.1, C106.1, FB101.1, R102.1, TP101.1, U102.3 (VI); also elsewhere on the board
/USB/USB_5V: C101.1, U101.6 (IN2); also elsewhere on the board
/microcontroller/PWR_INT1: J101.2; also elsewhere on the board
/microcontroller/PWR_INT2: J101.3; also elsewhere on the board
/microcontroller/SPI1_MISO: J101.5; also elsewhere on the board
/microcontroller/SPI1_MOSI: J101.4; also elsewhere on the board
/microcontroller/SPI1_NSS: J101.7; also elsewhere on the board
/microcontroller/SPI1_SCK: J101.6; also elsewhere on the board
GND: C101.2, C102.2, C103.2, C104.2, C105.2, C106.2, C107.2, D101.1 (K), D102.1 (K), H101.1, H102.1, H103.1, H104.1, J101.1, J102.1, R101.2, U101.3 (D1), U101.5 (GND), U102.1 (GND); also elsewhere on the board
unnamed: D101.2 (A), R103.2
unnamed: D102.2 (A), R104.2
unnamed: C105.1, J102.2, U101.8 (IN1)
unnamed: R102.2, R103.1
unnamed: R101.1, U101.4 (ILIM)
unnamed: C102.1, FB101.2, U101.7 (OUT)

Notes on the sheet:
Mounting holes
Power input
Power board communication (power board has pullups)
Tries first to power from connector, else USB
Main power consumers: MCU: ~150 mA uSD: ~100 mA RAM: ~70 mA Encoder: ~30 mA
3.3 V regulator
Sets current limit to 500 mA

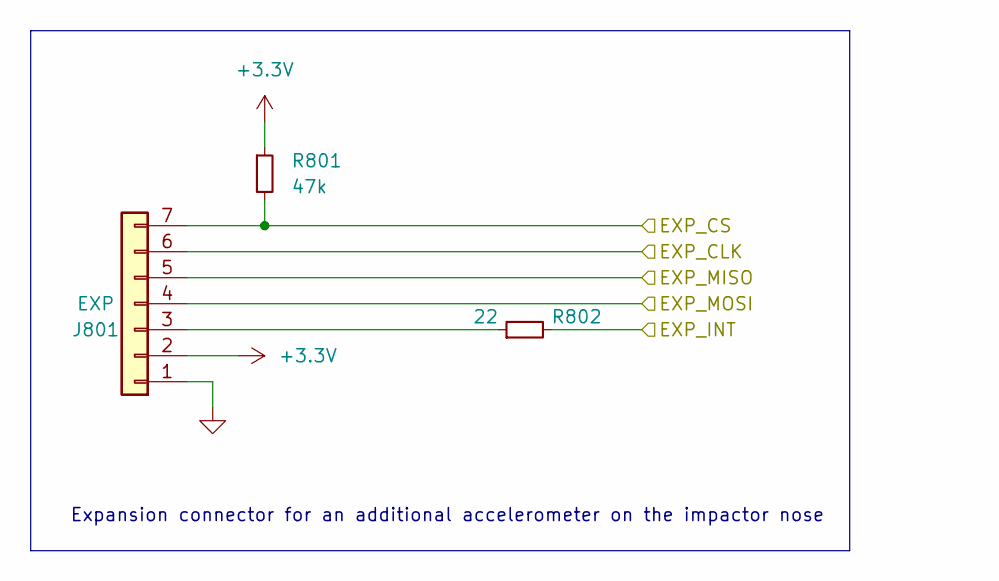
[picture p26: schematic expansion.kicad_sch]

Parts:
J801: EXP; JST_SH_SM07B-SRSS-TB_1x07-1MP_P1.00mm_Horizontal; LCSC C160406
R801: 47k; R_0402_1005Metric; LCSC C25792
R802: 22; R_0402_1005Metric; LCSC C25092

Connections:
+3.3V: J801.2, R801.1; also elsewhere on the board
/expansion/EXP_CLK: J801.6; also elsewhere on the board
/expansion/EXP_CS: J801.7, R801.2; also elsewhere on the board
/expansion/EXP_INT: R802.2; also elsewhere on the board
/expansion/EXP_MISO: J801.5; also elsewhere on the board
/expansion/EXP_MOSI: J801.4; also elsewhere on the board
GND: J801.1; also elsewhere on the board
unnamed: J801.3, R802.1

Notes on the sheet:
Expansion connector for an additional accelerometer on the impactor nose

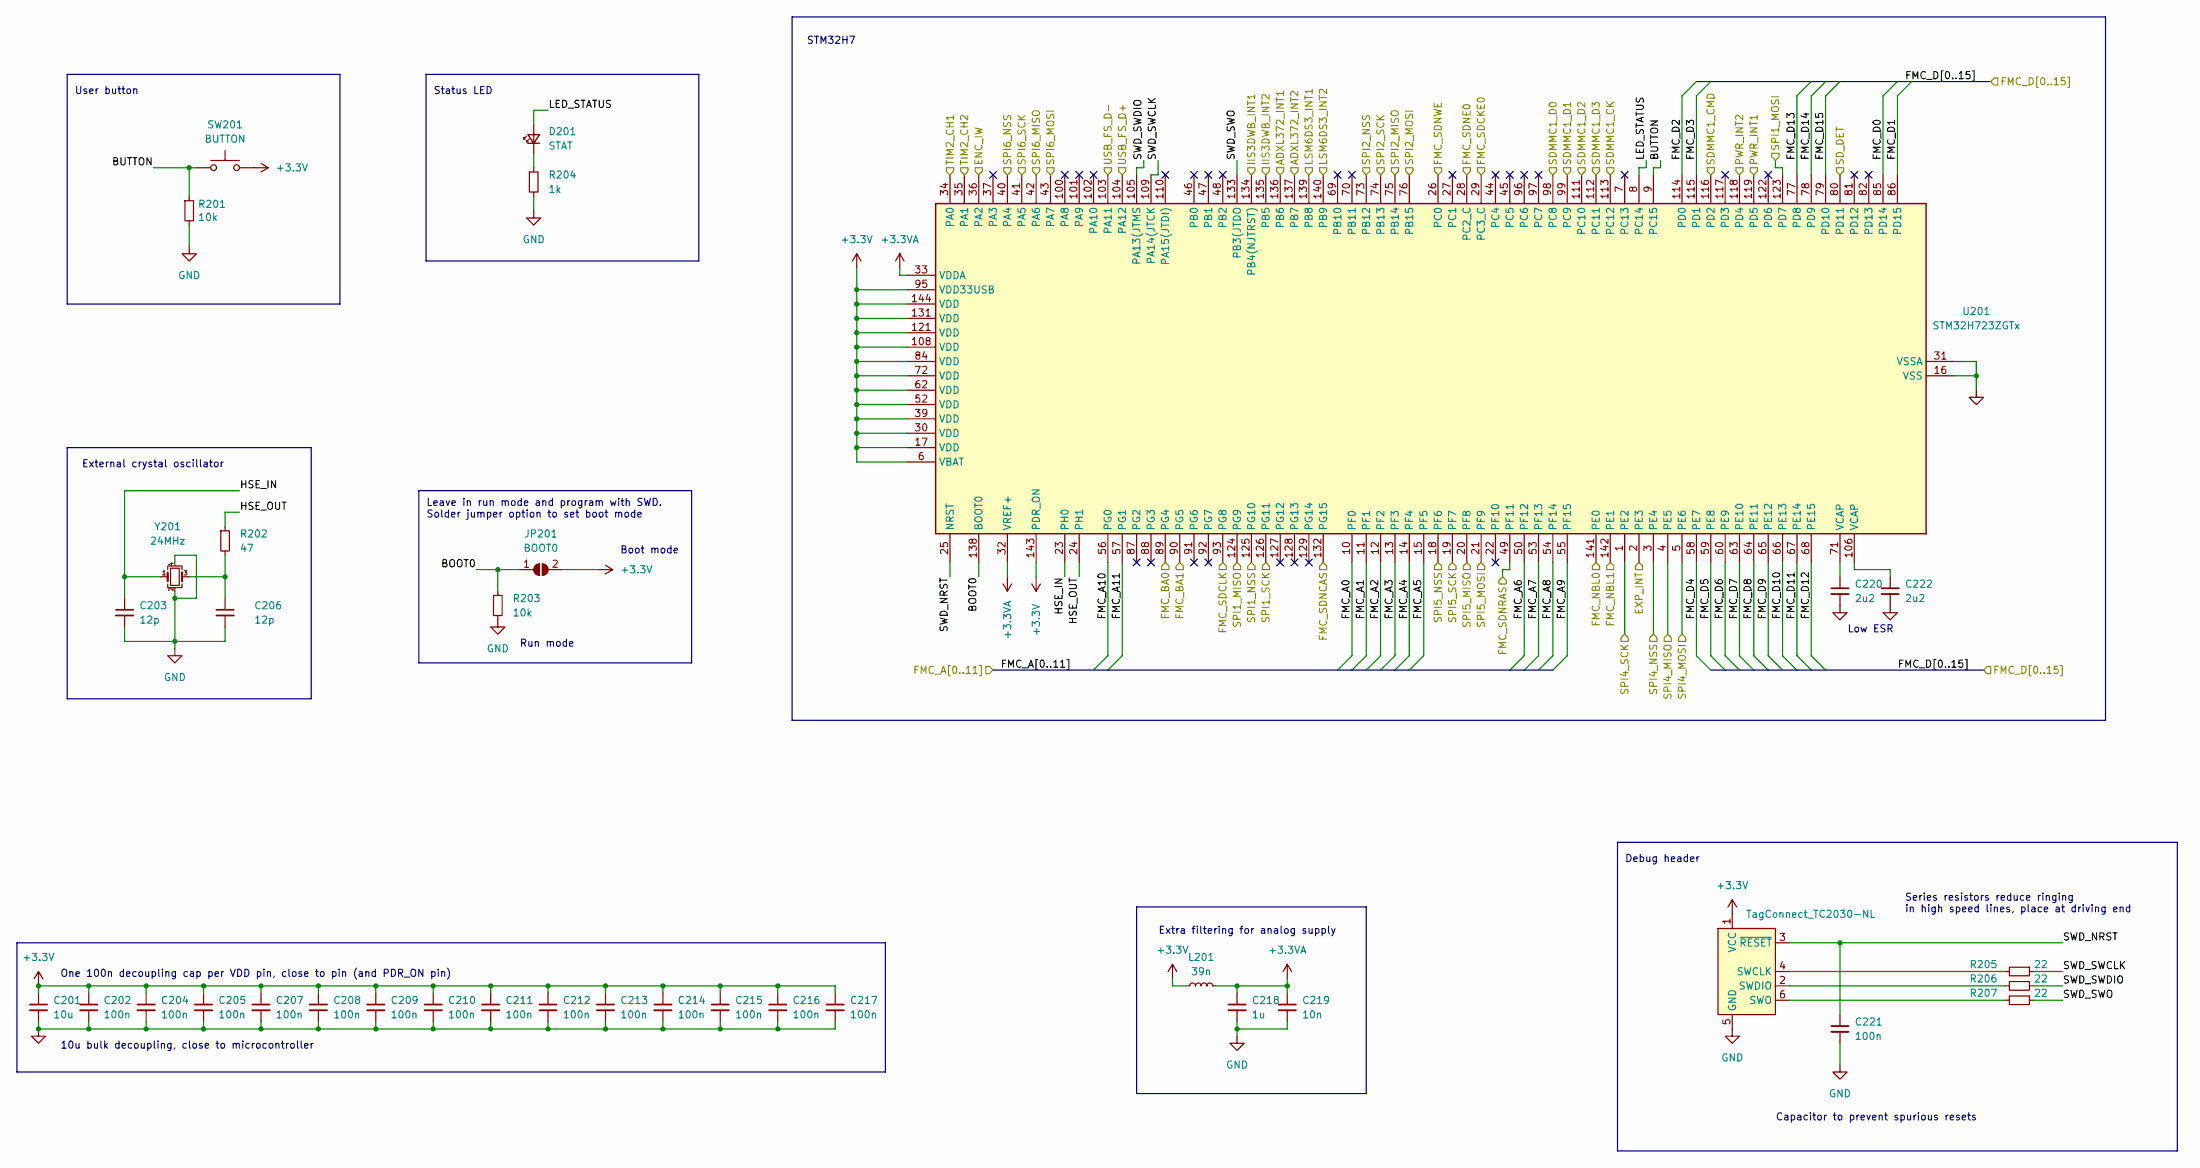
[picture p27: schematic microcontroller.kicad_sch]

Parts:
C201: 10u; C_0603_1608Metric; LCSC C19702
C202, C204, C205, C207, C208, C209, C210, C211, C212, C213, C214, C215, C216, C217, C221: 100n; C_0402_1005Metric; LCSC C1525
C203, C206: 12p; C_0402_1005Metric; LCSC C1547
C218: 1u; C_0402_1005Metric; LCSC C52923
C219: 10n; C_0402_1005Metric; LCSC C15195
C220, C222: 2u2; C_0603_1608Metric; LCSC C23630
D201: STAT; LED_0603_1608Metric; LCSC C84266
J201: TagConnect_TC2030-NL; Tag-Connect_TC2030-IDC-NL_2x03_P1.27mm_Vertical
JP201: BOOT0; SolderJumper-2_P1.3mm_Open_RoundedPad1.0x1.5mm
L201: 39n; L_0402_1005Metric; LCSC C26443
R201, R203: 10k; R_0402_1005Metric; LCSC C25744
R202: 47; R_0402_1005Metric; LCSC C25118
R204: 1k; R_0402_1005Metric; LCSC C11702
R205, R206, R207: 22; R_0402_1005Metric; LCSC C25092
SW201: BUTTON; SW_Push_SPST_NO_Alps_SKRK; LCSC C202388
U201: STM32H723ZGTx; LQFP-144_20x20mm_P0.5mm; LCSC C730146
Y201: 24MHz; Crystal_SMD_3225-4Pin_3.2x2.5mm; LCSC C70590

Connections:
+3.3V: C201.1, C202.1, C204.1, C205.1, C207.1, C208.1, C209.1, C210.1, C211.1, C212.1, C213.1, C214.1, C215.1, C216.1, C217.1, J201.1 (VCC), JP201.2 (B), L201.1, SW201.2, U201.6 (VBAT), U201.17 (VDD), U201.30 (VDD), U201.39 (VDD), U201.52 (VDD), U201.62 (VDD), U201.72 (VDD), U201.84 (VDD), U201.95 (VDD33USB), U201.108 (VDD), U201.121 (VDD), U201.131 (VDD), U201.143 (PDR_ON), U201.144 (VDD); also elsewhere on the board
+3.3VA: C218.1, C219.1, L201.2, U201.32 (VREF+), U201.33 (VDDA)
/SDRAM/A0: U201.10 (PF0); also elsewhere on the board
/SDRAM/A1: U201.11 (PF1); also elsewhere on the board
/SDRAM/A2: U201.12 (PF2); also elsewhere on the board
/SDRAM/A3: U201.13 (PF3); also elsewhere on the board
/SDRAM/A4: U201.14 (PF4); also elsewhere on the board
/SDRAM/A5: U201.15 (PF5); also elsewhere on the board
/SDRAM/A6: U201.50 (PF12); also elsewhere on the board
/SDRAM/A7: U201.53 (PF13); also elsewhere on the board
/SDRAM/A8: U201.54 (PF14); also elsewhere on the board
/SDRAM/A9: U201.55 (PF15); also elsewhere on the board
/SDRAM/A10: U201.56 (PG0); also elsewhere on the board
/SDRAM/A11: U201.57 (PG1); also elsewhere on the board
/SDRAM/BS0: U201.89 (PG4); also elsewhere on the board
/SDRAM/BS1: U201.90 (PG5); also elsewhere on the board
/SDRAM/CKE: U201.29 (PC3_C); also elsewhere on the board
/SDRAM/CLK: U201.93 (PG8); also elsewhere on the board
/SDRAM/DQ0: U201.85 (PD14); also elsewhere on the board
/SDRAM/DQ1: U201.86 (PD15); also elsewhere on the board
/SDRAM/DQ2: U201.114 (PD0); also elsewhere on the board
/SDRAM/DQ3: U201.115 (PD1); also elsewhere on the board
/SDRAM/DQ4: U201.58 (PE7); also elsewhere on the board
/SDRAM/DQ5: U201.59 (PE8); also elsewhere on the board
/SDRAM/DQ6: U201.60 (PE9); also elsewhere on the board
/SDRAM/DQ7: U201.63 (PE10); also elsewhere on the board
/SDRAM/DQ8: U201.64 (PE11); also elsewhere on the board
/SDRAM/DQ9: U201.65 (PE12); also elsewhere on the board
/SDRAM/DQ10: U201.66 (PE13); also elsewhere on the board
/SDRAM/DQ11: U201.67 (PE14); also elsewhere on the board
/SDRAM/DQ12: U201.68 (PE15); also elsewhere on the board
/SDRAM/DQ13: U201.77 (PD8); also elsewhere on the board
/SDRAM/DQ14: U201.78 (PD9); also elsewhere on the board
/SDRAM/DQ15: U201.79 (PD10); also elsewhere on the board
/SDRAM/LDQM: U201.141 (PE0); also elsewhere on the board
/SDRAM/NCAS: U201.132 (PG15); also elsewhere on the board
/SDRAM/NCS: U201.28 (PC2_C); also elsewhere on the board
/SDRAM/NRAS: U201.49 (PF11); also elsewhere on the board
/SDRAM/NWE: U201.26 (PC0); also elsewhere on the board
/SDRAM/UDQM: U201.142 (PE1); also elsewhere on the board
/USB/USB_D+: U201.104 (PA12); also elsewhere on the board
/USB/USB_D-: U201.103 (PA11); also elsewhere on the board
/accelerometer/ADXL372_CLK: U201.74 (PB13); also elsewhere on the board
/accelerometer/ADXL372_CS: U201.73 (PB12); also elsewhere on the board
/accelerometer/ADXL372_INT1: U201.136 (PB6); also elsewhere on the board
/accelerometer/ADXL372_INT2: U201.137 (PB7); also elsewhere on the board
/accelerometer/ADXL372_MISO: U201.75 (PB14); also elsewhere on the board
/accelerometer/ADXL372_MOSI: U201.76 (PB15); also elsewhere on the board
/accelerometer/IIS3DWB_CLK: U201.41 (PA5); also elsewhere on the board
/accelerometer/IIS3DWB_CS: U201.40 (PA4); also elsewhere on the board
/accelerometer/IIS3DWB_INT1: U201.134 (PB4(NJTRST)); also elsewhere on the board
/accelerometer/IIS3DWB_INT2: U201.135 (PB5); also elsewhere on the board
/accelerometer/IIS3DWB_MISO: U201.42 (PA6); also elsewhere on the board
/accelerometer/IIS3DWB_MOSI: U201.43 (PA7); also elsewhere on the board
/accelerometer/LSM6DS3_CLK: U201.19 (PF7); also elsewhere on the board
/accelerometer/LSM6DS3_CS: U201.18 (PF6); also elsewhere on the board
/accelerometer/LSM6DS3_INT1: U201.139 (PB8); also elsewhere on the board
/accelerometer/LSM6DS3_INT2: U201.140 (PB9); also elsewhere on the board
/accelerometer/LSM6DS3_MISO: U201.20 (PF8); also elsewhere on the board
/accelerometer/LSM6DS3_MOSI: U201.21 (PF9); also elsewhere on the board
/encoder/ENC_A: U201.34 (PA0); also elsewhere on the board
/encoder/ENC_B: U201.35 (PA1); also elsewhere on the board
/encoder/ENC_IW: U201.36 (PA2); also elsewhere on the board
/expansion/EXP_CLK: U201.1 (PE2); also elsewhere on the board
/expansion/EXP_CS: U201.3 (PE4); also elsewhere on the board
/expansion/EXP_INT: U201.2 (PE3); also elsewhere on the board
/expansion/EXP_MISO: U201.4 (PE5); also elsewhere on the board
/expansion/EXP_MOSI: U201.5 (PE6); also elsewhere on the board
/microcontroller/BOOT0: JP201.1 (A), R203.1, U201.138 (BOOT0)
/microcontroller/BUTTON: R201.1, SW201.1, U201.9 (PC15)
/microcontroller/HSE_IN: C203.1, U201.23 (PH0), Y201.1
/microcontroller/HSE_OUT: R202.1, U201.24 (PH1)
/microcontroller/LED_STATUS: D201.2 (A), U201.8 (PC14)
/microcontroller/PWR_INT1: U201.119 (PD5); also elsewhere on the board
/microcontroller/PWR_INT2: U201.118 (PD4); also elsewhere on the board
/microcontroller/SDMMC1_CK: U201.113 (PC12); also elsewhere on the board
/microcontroller/SDMMC1_CMD: U201.116 (PD2); also elsewhere on the board
/microcontroller/SDMMC1_D0: U201.98 (PC8); also elsewhere on the board
/microcontroller/SDMMC1_D1: U201.99 (PC9); also elsewhere on the board
/microcontroller/SDMMC1_D2: U201.111 (PC10); also elsewhere on the board
/microcontroller/SDMMC1_D3: U201.112 (PC11); also elsewhere on the board
/microcontroller/SD_DET: U201.80 (PD11); also elsewhere on the board
/microcontroller/SPI1_MISO: U201.124 (PG9); also elsewhere on the board
/microcontroller/SPI1_MOSI: U201.123 (PD7); also elsewhere on the board
/microcontroller/SPI1_NSS: U201.125 (PG10); also elsewhere on the board
/microcontroller/SPI1_SCK: U201.126 (PG11); also elsewhere on the board
/microcontroller/SWD_NRST: C221.1, J201.3 (~RESET), U201.25 (NRST)
/microcontroller/SWD_SWCLK: R205.1, U201.109 (PA14(JTCK)
/microcontroller/SWD_SWDIO: R206.1, U201.105 (PA13(JTMS)
/microcontroller/SWD_SWO: R207.1, U201.133 (PB3(JTDO)
GND: C201.2, C202.2, C203.2, C204.2, C205.2, C206.2, C207.2, C208.2, C209.2, C210.2, C211.2, C212.2, C213.2, C214.2, C215.2, C216.2, C217.2, C218.2, C219.2, C220.2, C221.2, C222.2, J201.5 (GND), R201.2, R203.2, R204.2, U201.16 (VSS), U201.31 (VSSA), U201.38 (VSS), U201.51 (VSS), U201.61 (VSS), U201.83 (VSS), U201.94 (VSS), U201.107 (VSS), U201.120 (VSS), U201.130 (VSS), Y201.2, Y201.4; also elsewhere on the board
unnamed: C206.1, R202.2, Y201.3
unnamed: C220.1, U201.71 (VCAP)
unnamed: C222.1, U201.106 (VCAP)
unnamed: D201.1 (K), R204.1
unnamed: J201.4 (SWCLK), R205.2
unnamed: J201.2 (SWDIO), R206.2
unnamed: J201.6 (SWO), R207.2

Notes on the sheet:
Debug header
Run mode
Leave in run mode and program with SWD. Solder jumper option to set boot mode
User button
Low ESR
Extra filtering for analog supply
One 100n decoupling cap per VDD pin, close to pin (and PDR_ON pin)
Boot mode
Status LED
External crystal oscillator
Capacitor to prevent spurious resets
STM32H7
Series resistors reduce ringing in high speed lines, place at driving end
10u bulk decoupling, close to microcontroller

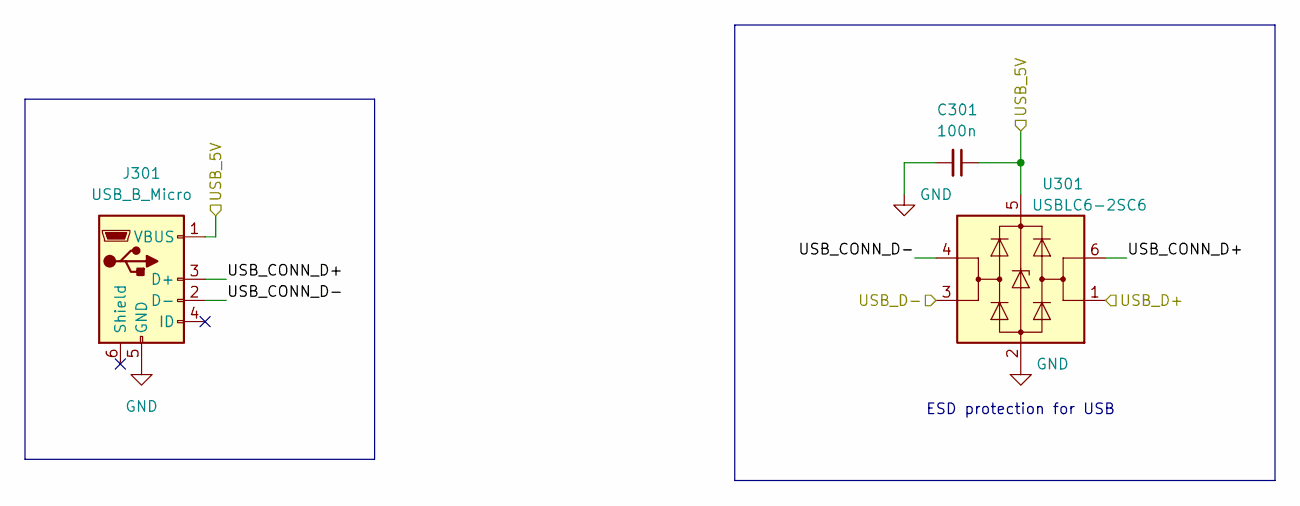
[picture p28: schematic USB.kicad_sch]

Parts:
C301: 100n; C_0402_1005Metric; LCSC C1525
J301: USB_B_Micro; MicroXNJ; LCSC C404969
U301: USBLC6-2SC6; SOT-23-6; LCSC C2827654

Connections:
/USB/USB_5V: C301.1, J301.1 (VBUS), U301.5 (VBUS); also elsewhere on the board
/USB/USB_CONN_D+: J301.3 (D+), U301.6 (I/O1)
/USB/USB_CONN_D-: J301.2 (D-), U301.4 (I/O2)
/USB/USB_D+: U301.1 (I/O1); also elsewhere on the board
/USB/USB_D-: U301.3 (I/O2); also elsewhere on the board
GND: C301.2, J301.5 (GND), U301.2 (GND); also elsewhere on the board

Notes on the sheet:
ESD protection for USB

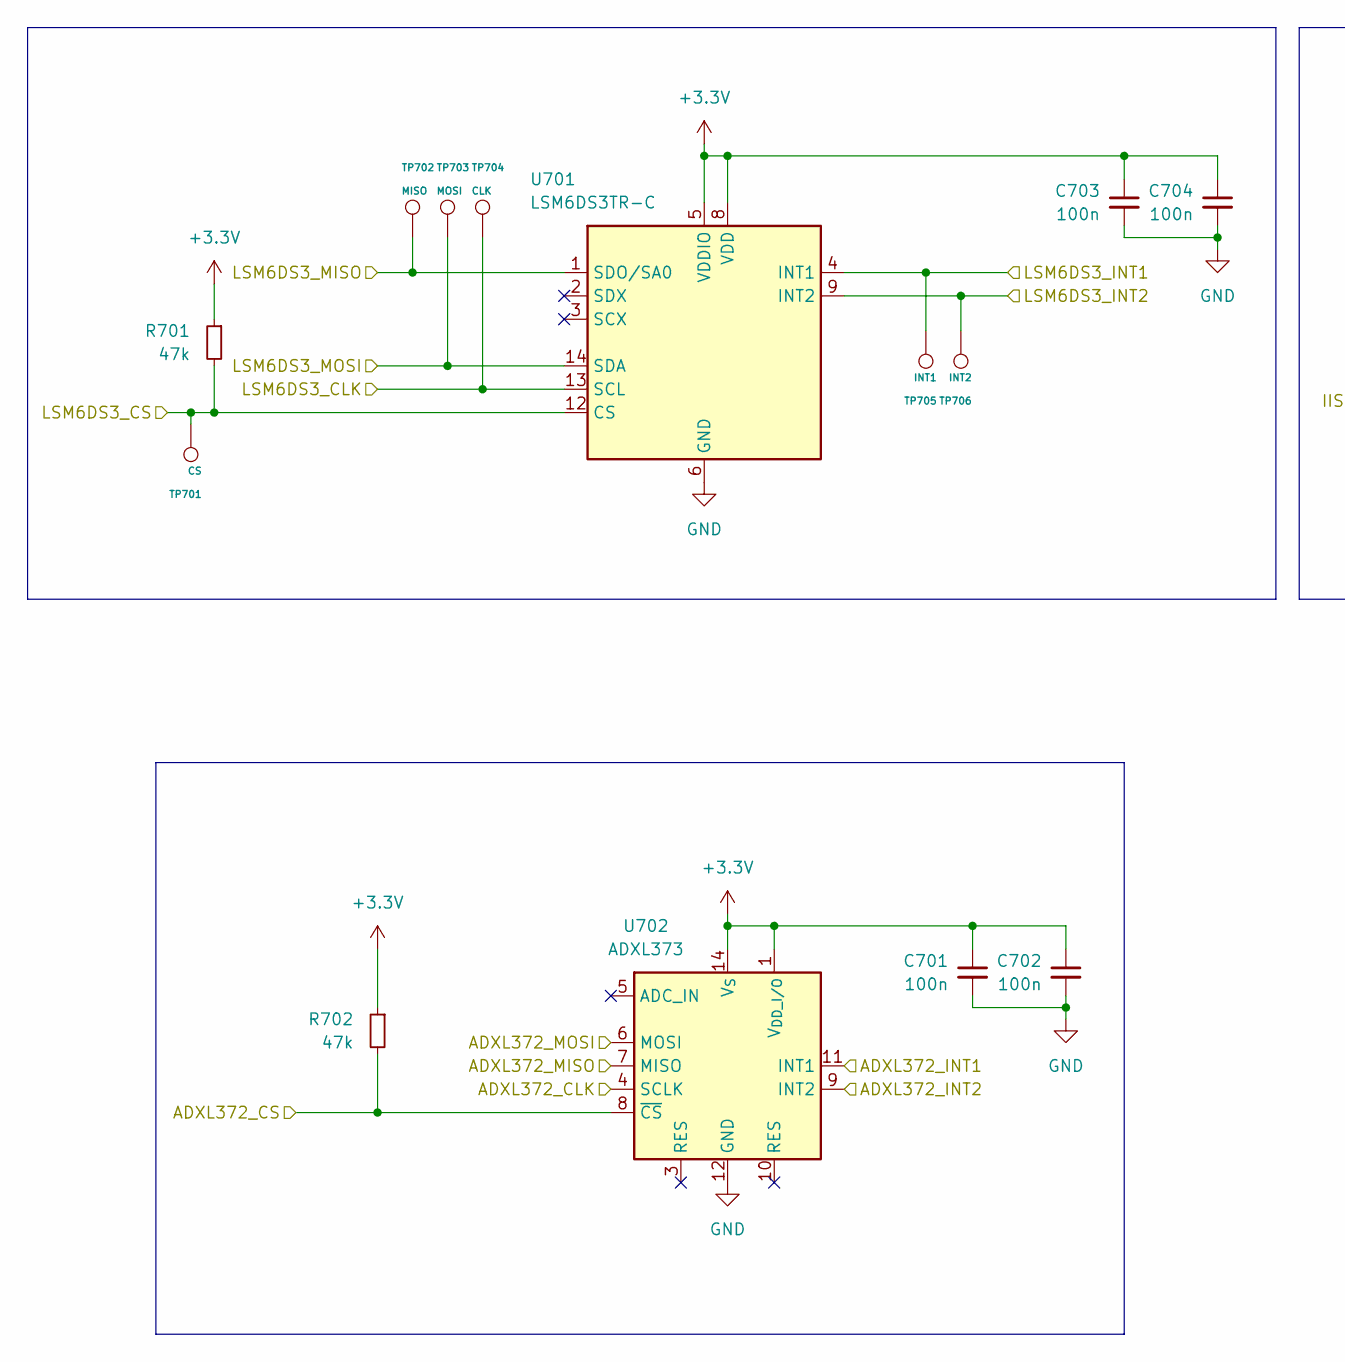
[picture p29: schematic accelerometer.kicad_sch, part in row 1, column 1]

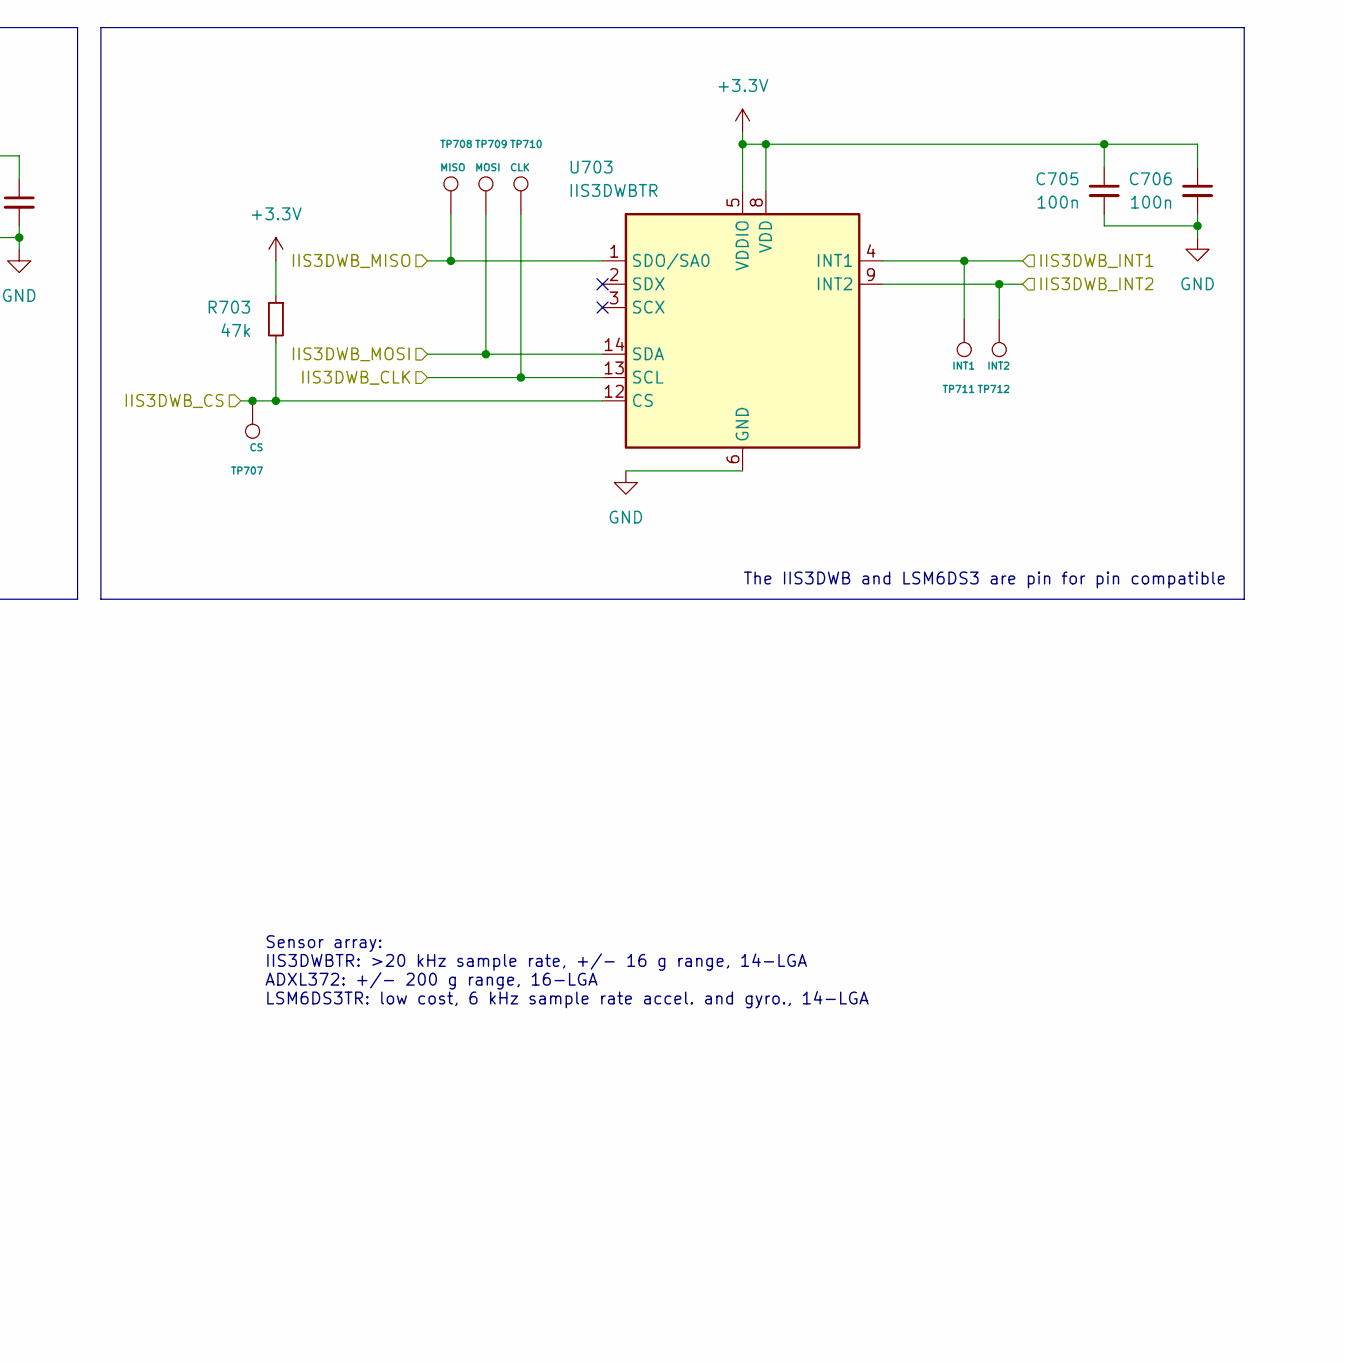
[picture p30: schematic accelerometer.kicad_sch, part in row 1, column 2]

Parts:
C701, C702, C703, C704, C705, C706: 100n; C_0402_1005Metric; LCSC C1525
R701, R702, R703: 47k; R_0402_1005Metric; LCSC C25792
TP701, TP707: CS; TestPoint_Pad_D1.0mm
TP702, TP708: MISO; TestPoint_Pad_D1.0mm
TP703, TP709: MOSI; TestPoint_Pad_D1.0mm
TP704, TP710: CLK; TestPoint_Pad_D1.0mm
TP705, TP711: INT1; TestPoint_Pad_D1.0mm
TP706, TP712: INT2; TestPoint_Pad_D1.0mm
U701: LSM6DS3TR-C; LGA-14_3x2.5mm_P0.5mm_LayoutBorder3x4y; LCSC C967633
U702: ADXL373; Analog_LGA-16_3.25x3mm_P0.5mm_LayoutBorder3x5y; LCSC C3216386
U703: IIS3DWBTR; LGA-14_3x2.5mm_P0.5mm_LayoutBorder3x4y; LCSC C717702

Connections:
+3.3V: C701.1, C702.1, C703.1, C704.1, C705.1, C706.1, R701.1, R702.1, R703.1, U701.5 (VDDIO), U701.8 (VDD), U702.1 (V_{DD_I/O}), U702.14 (V_{S}), U703.5 (VDDIO), U703.8 (VDD); also elsewhere on the board
/accelerometer/ADXL372_CLK: U702.4 (SCLK); also elsewhere on the board
/accelerometer/ADXL372_CS: R702.2, U702.8 (~CS); also elsewhere on the board
/accelerometer/ADXL372_INT1: U702.11 (INT1); also elsewhere on the board
/accelerometer/ADXL372_INT2: U702.9 (INT2); also elsewhere on the board
/accelerometer/ADXL372_MISO: U702.7 (MISO); also elsewhere on the board
/accelerometer/ADXL372_MOSI: U702.6 (MOSI); also elsewhere on the board
/accelerometer/IIS3DWB_CLK: TP710.1, U703.13 (SCL); also elsewhere on the board
/accelerometer/IIS3DWB_CS: R703.2, TP707.1, U703.12 (CS); also elsewhere on the board
/accelerometer/IIS3DWB_INT1: TP711.1, U703.4 (INT1); also elsewhere on the board
/accelerometer/IIS3DWB_INT2: TP712.1, U703.9 (INT2); also elsewhere on the board
/accelerometer/IIS3DWB_MISO: TP708.1, U703.1 (SDO/SA0); also elsewhere on the board
/accelerometer/IIS3DWB_MOSI: TP709.1, U703.14 (SDA); also elsewhere on the board
/accelerometer/LSM6DS3_CLK: TP704.1, U701.13 (SCL); also elsewhere on the board
/accelerometer/LSM6DS3_CS: R701.2, TP701.1, U701.12 (CS); also elsewhere on the board
/accelerometer/LSM6DS3_INT1: TP705.1, U701.4 (INT1); also elsewhere on the board
/accelerometer/LSM6DS3_INT2: TP706.1, U701.9 (INT2); also elsewhere on the board
/accelerometer/LSM6DS3_MISO: TP702.1, U701.1 (SDO/SA0); also elsewhere on the board
/accelerometer/LSM6DS3_MOSI: TP703.1, U701.14 (SDA); also elsewhere on the board
GND: C701.2, C702.2, C703.2, C704.2, C705.2, C706.2, U701.6 (GND), U701.7 (GND), U702.12 (GND), U702.13 (GND), U702.16 (GND), U703.6 (GND), U703.7 (GND); also elsewhere on the board

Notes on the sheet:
Sensor array: IIS3DWBTR: >20 kHz sample rate, +/- 16 g range, 14-LGA ADXL372: +/- 200 g range, 16-LGA LSM6DS3TR: low cost, 6 kHz sample rate accel. and gyro., 14-LGA
The IIS3DWB and LSM6DS3 are pin for pin compatible

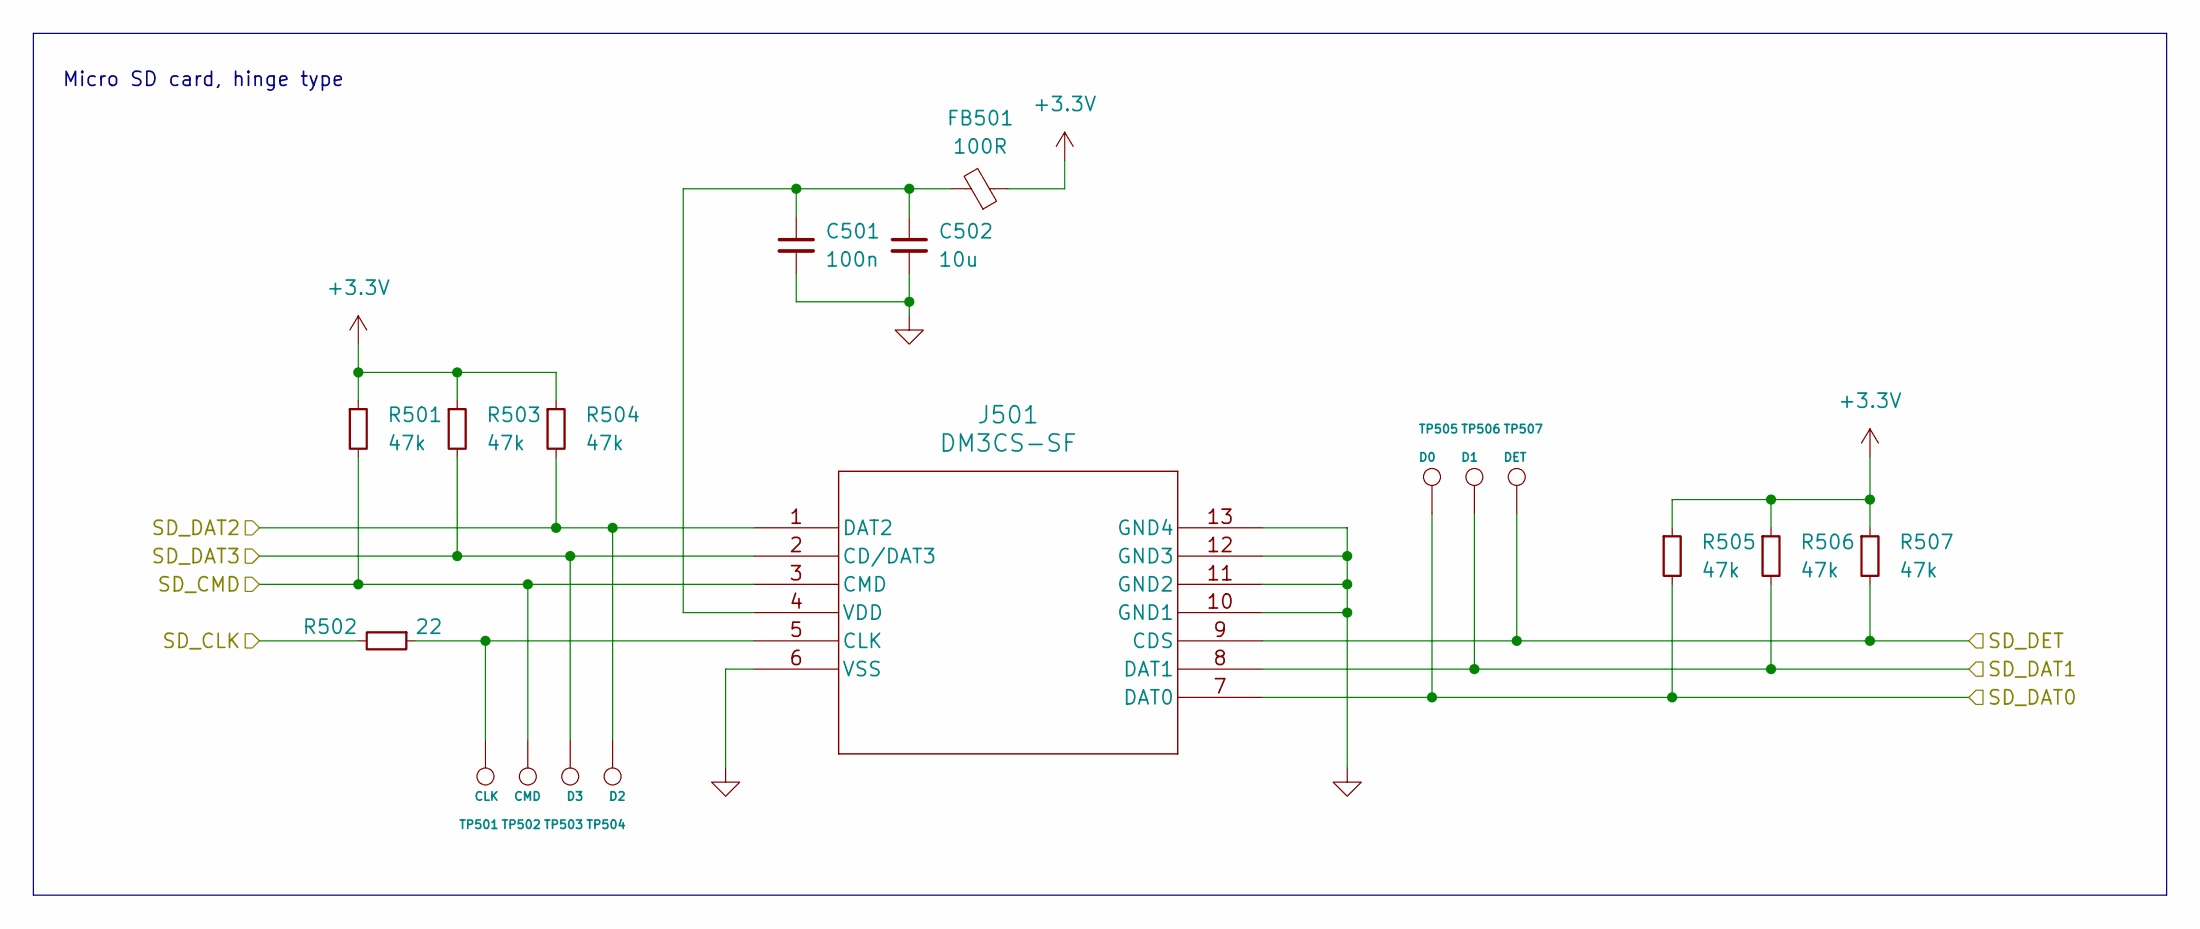
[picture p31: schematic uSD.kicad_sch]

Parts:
C501: 100n; C_0402_1005Metric; LCSC C1525
C502: 10u; C_0603_1608Metric; LCSC C19702
FB501: 100R; L_0603_1608Metric; LCSC C1002
J501: DM3CS-SF; DM3CS-SF_HIR; LCSC C202111
R501, R503, R504, R505, R506, R507: 47k; R_0402_1005Metric; LCSC C25792
R502: 22; R_0402_1005Metric; LCSC C25092
TP501: CLK; TestPoint_Pad_D1.0mm
TP502: CMD; TestPoint_Pad_D1.0mm
TP503: D3; TestPoint_Pad_D1.0mm
TP504: D2; TestPoint_Pad_D1.0mm
TP505: D0; TestPoint_Pad_D1.0mm
TP506: D1; TestPoint_Pad_D1.0mm
TP507: DET; TestPoint_Pad_D1.0mm

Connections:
+3.3V: FB501.1, R501.1, R503.1, R504.1, R505.1, R506.1, R507.1; also elsewhere on the board
/microcontroller/SDMMC1_CK: R502.2; also elsewhere on the board
/microcontroller/SDMMC1_CMD: J501.3 (CMD), R501.2, TP502.1; also elsewhere on the board
/microcontroller/SDMMC1_D0: J501.7 (DAT0), R505.2, TP505.1; also elsewhere on the board
/microcontroller/SDMMC1_D1: J501.8 (DAT1), R506.2, TP506.1; also elsewhere on the board
/microcontroller/SDMMC1_D2: J501.1 (DAT2), R504.2, TP504.1; also elsewhere on the board
/microcontroller/SDMMC1_D3: J501.2 (CD/DAT3), R503.2, TP503.1; also elsewhere on the board
/microcontroller/SD_DET: J501.9 (CDS), R507.2, TP507.1; also elsewhere on the board
GND: C501.2, C502.2, J501.6 (VSS), J501.10 (GND1), J501.11 (GND2), J501.12 (GND3), J501.13 (GND4); also elsewhere on the board
unnamed: J501.5 (CLK), R502.1, TP501.1
unnamed: C501.1, C502.1, FB501.2, J501.4 (VDD)

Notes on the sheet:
Micro SD card, hinge type

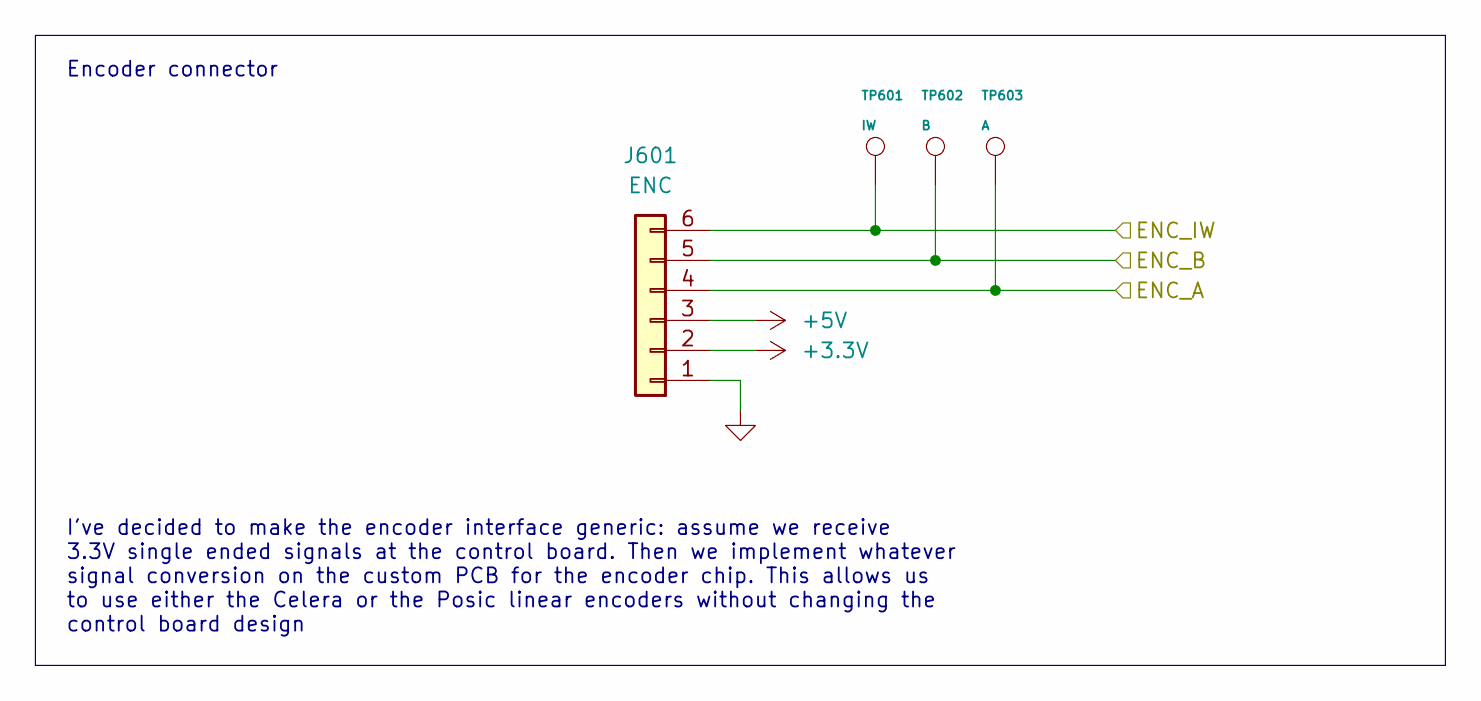
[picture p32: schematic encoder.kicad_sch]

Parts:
J601: ENC; JST_SH_SM06B-SRSS-TB_1x06-1MP_P1.00mm_Horizontal; LCSC C160405
TP601: IW; TestPoint_Pad_D1.0mm
TP602: B; TestPoint_Pad_D1.0mm
TP603: A; TestPoint_Pad_D1.0mm

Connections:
+3.3V: J601.2; also elsewhere on the board
+5V: J601.3; also elsewhere on the board
/encoder/ENC_A: J601.4, TP603.1; also elsewhere on the board
/encoder/ENC_B: J601.5, TP602.1; also elsewhere on the board
/encoder/ENC_IW: J601.6, TP601.1; also elsewhere on the board
GND: J601.1; also elsewhere on the board

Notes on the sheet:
Encoder connector
I've decided to make the encoder interface generic: assume we receive 3.3V single ended signals at the control board. Then we implement whatever signal conversion on the custom PCB for the encoder chip. This allows us to use either the Celera or the Posic linear encoders without changing the contro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

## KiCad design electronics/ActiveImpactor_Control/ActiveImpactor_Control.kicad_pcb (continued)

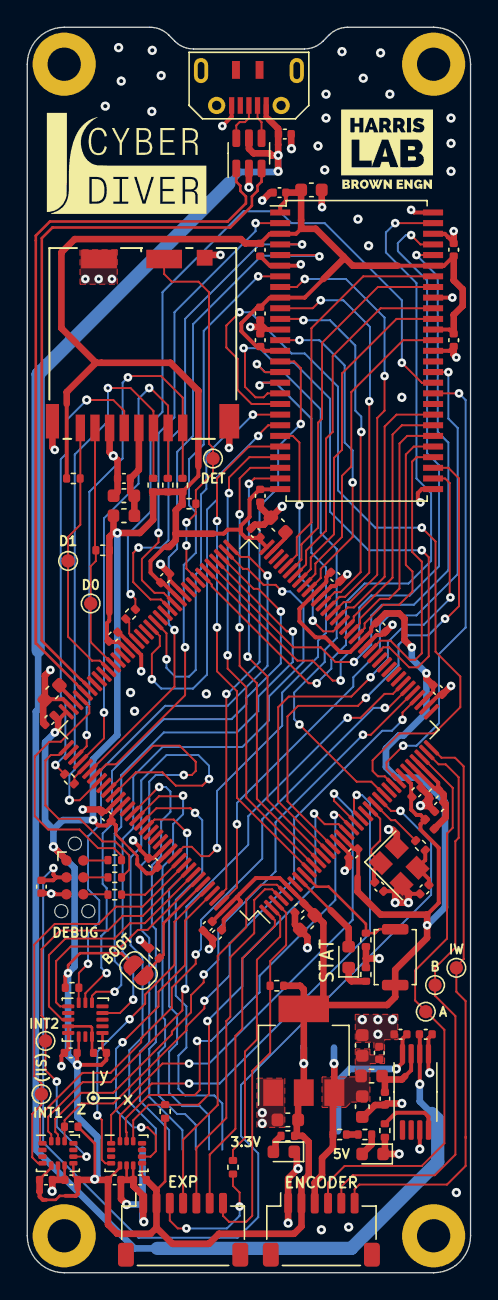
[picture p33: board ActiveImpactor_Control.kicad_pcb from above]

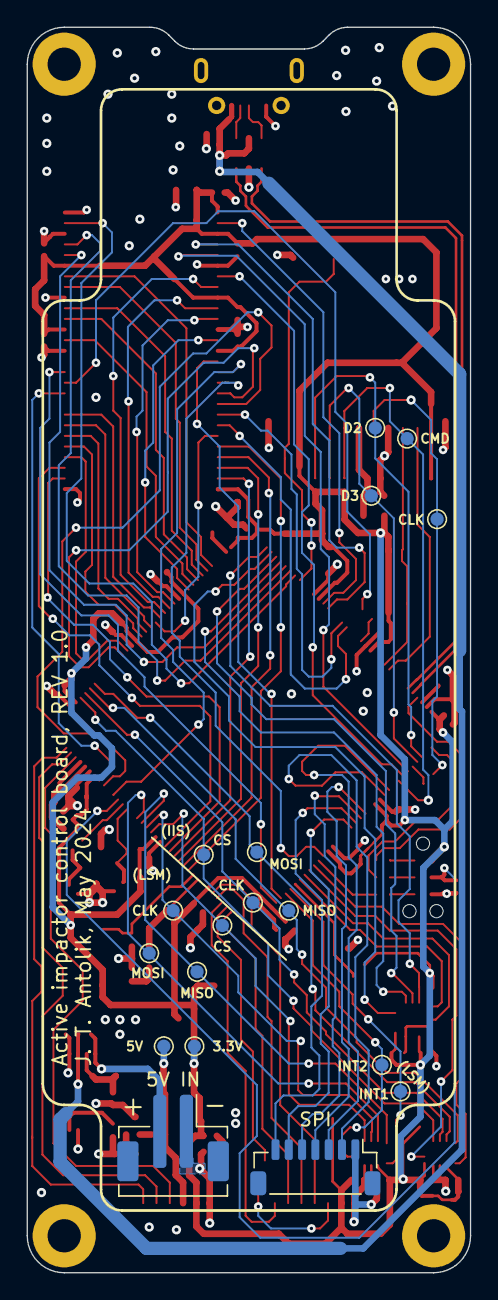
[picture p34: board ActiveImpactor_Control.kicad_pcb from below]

Board: 4 copper layers, 33.3 x 93.7 mm, 122 parts (18 on the bottom side), 112 nets.

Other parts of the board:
C401: 10u; C_0603_1608Metric
C402, C403, C404, C405, C406, C407, C408: 100n; C_0402_1005Metric
R401: 22; R_0402_1005Metric
U401: W9812G6KH-6; TSOP-II-54_22.2x10.16mm_P0.8mm

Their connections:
+3.3V: C401.1, C402.1, C403.1, C404.1, C405.1, C406.1, C407.1, C408.1, U401.1 (VDD), U401.3 (VDDQ), U401.9 (VDDQ), U401.14 (VDD), U401.27 (VDD), U401.43 (VDDQ), U401.49 (VDDQ); also elsewhere on the board
/SDRAM/A0: U401.23 (A0); also elsewhere on the board
/SDRAM/A1: U401.24 (A1); also elsewhere on the board
/SDRAM/A2: U401.25 (A2); also elsewhere on the board
/SDRAM/A3: U401.26 (A3); also elsewhere on the board
/SDRAM/A4: U401.29 (A4); also elsewhere on the board
/SDRAM/A5: U401.30 (A5); also elsewhere on the board
/SDRAM/A6: U401.31 (A6); also elsewhere on the board
/SDRAM/A7: U401.32 (A7); also elsewhere on the board
/SDRAM/A8: U401.33 (A8); also elsewhere on the board
/SDRAM/A9: U401.34 (A9); also elsewhere on the board
/SDRAM/A10: U401.22 (A10/AP); also elsewhere on the board
/SDRAM/A11: U401.35 (A11); also elsewhere on the board
/SDRAM/BS0: U401.20 (BS0); also elsewhere on the board
/SDRAM/BS1: U401.21 (BS1); also elsewhere on the board
/SDRAM/CKE: U401.37 (CKE); also elsewhere on the board
/SDRAM/CLK: R401.2; also elsewhere on the board
/SDRAM/DQ0: U401.2 (DQ0); also elsewhere on the board
/SDRAM/DQ1: U401.4 (DQ1); also elsewhere on the board
/SDRAM/DQ2: U401.5 (DQ2); also elsewhere on the board
/SDRAM/DQ3: U401.7 (DQ3); also elsewhere on the board
/SDRAM/DQ4: U401.8 (DQ4); also elsewhere on the board
/SDRAM/DQ5: U401.10 (DQ5); also elsewhere on the board
/SDRAM/DQ6: U401.11 (DQ6); also elsewhere on the board
/SDRAM/DQ7: U401.13 (DQ7); also elsewhere on the board
/SDRAM/DQ8: U401.42 (DQ8); also elsewhere on the board
/SDRAM/DQ9: U401.44 (DQ9); also elsewhere on the board
/SDRAM/DQ10: U401.45 (DQ10); also elsewhere on the board
/SDRAM/DQ11: U401.47 (DQ11); also elsewhere on the board
/SDRAM/DQ12: U401.48 (DQ12); also elsewhere on the board
/SDRAM/DQ13: U401.50 (DQ13); also elsewhere on the board
/SDRAM/DQ14: U401.51 (DQ14); also elsewhere on the board
/SDRAM/DQ15: U401.53 (DQ15); also elsewhere on the board
/SDRAM/LDQM: U401.15 (LDQM); also elsewhere on the board
/SDRAM/NCAS: U401.17 (~CAS); also elsewhere on the board
/SDRAM/NCS: U401.19 (~CS); also elsewhere on the board
/SDRAM/NRAS: U401.18 (~RAS); also elsewhere on the board
/SDRAM/NWE: U401.16 (~WE); also elsewhere on the board
/SDRAM/UDQM: U401.39 (UDQM); also elsewhere on the board
GND: C401.2, C402.2, C403.2, C404.2, C405.2, C406.2, C407.2, C408.2, U401.6 (VSSQ), U401.12 (VSSQ), U401.28 (VSS), U401.41 (VSS), U401.46 (VSSQ), U401.52 (VSSQ), U401.54 (VSS); also elsewhere on the board
unnamed: R401.1, U401.38 (CLK)

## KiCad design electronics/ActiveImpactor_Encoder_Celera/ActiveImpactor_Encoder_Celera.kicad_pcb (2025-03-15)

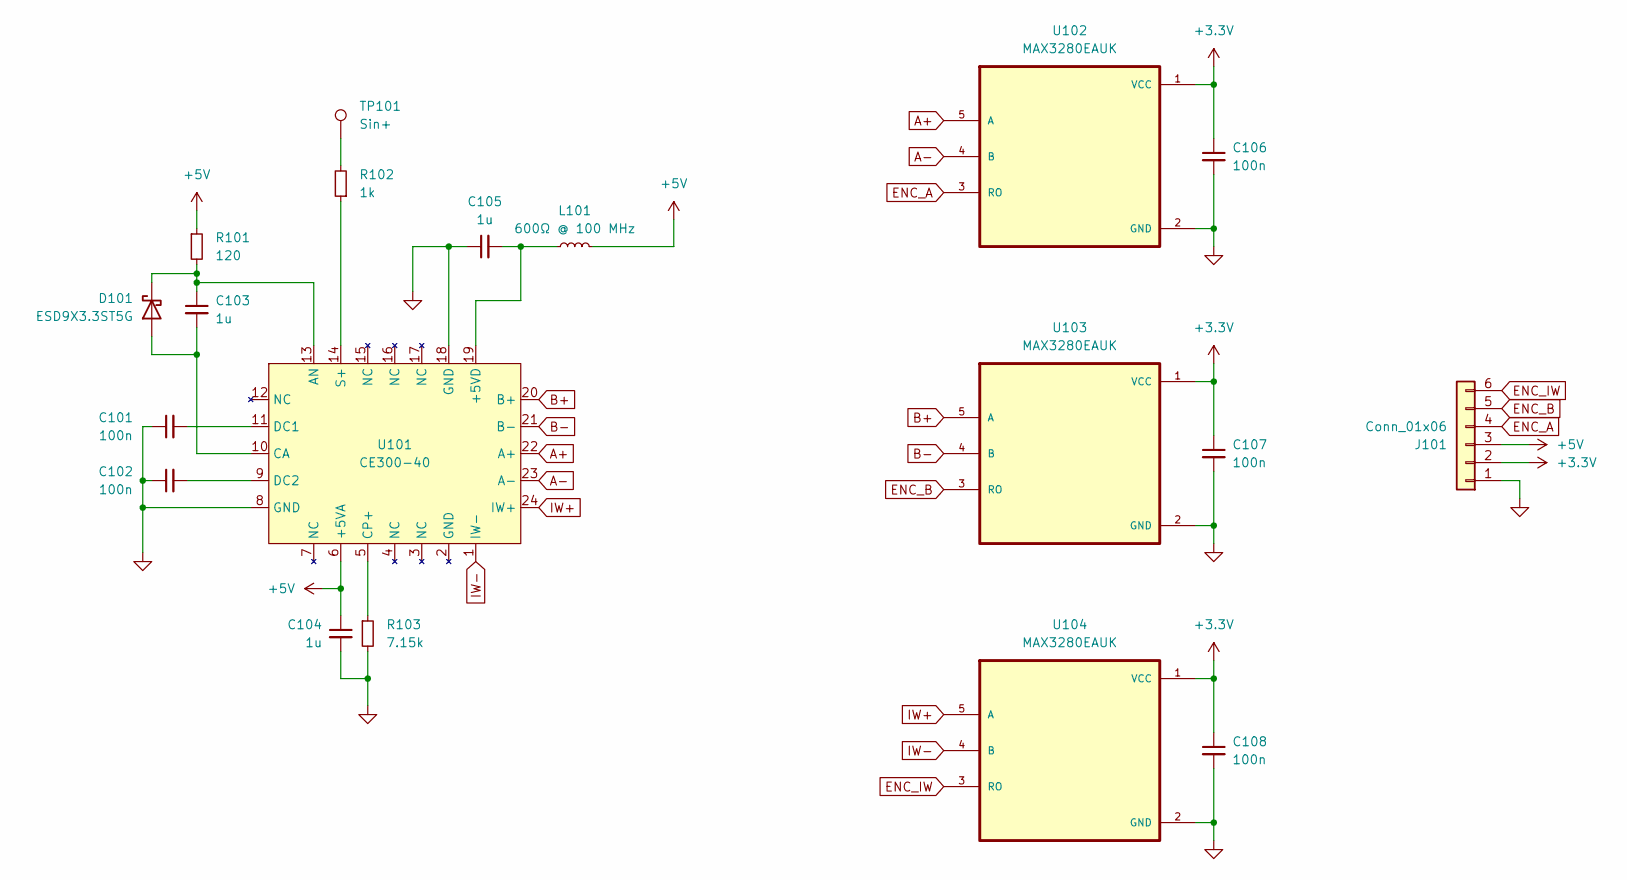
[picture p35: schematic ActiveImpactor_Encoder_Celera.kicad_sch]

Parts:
C101, C102, C106, C107, C108: 100n; C_0402_1005Metric; LCSC C1525
C103, C104, C105: 1u; C_0603_1608Metric; LCSC C15849
D101: ESD9X3.3ST5G; D_SOD-923; LCSC C130456
J101: Conn_01x06; JST_SH_BM06B-SRSS-TB_1x06-1MP_P1.00mm_Vertical; LCSC C160392
L101: 600Ω @ 100 MHz; L_0603_1608Metric; LCSC C19330
R101: 120; R_0402_1005Metric; LCSC C25079
R102: 1k; R_0402_1005Metric; LCSC C11702
R103: 7.15k; R_0402_1005Metric; LCSC C270586
TP101: Sin+; TestPoint_Pad_D1.5mm
U101: CE300-40
U102, U103, U104: MAX3280EAUK; SOT-23-5; LCSC C131126

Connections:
+3.3V: C106.1, C107.1, C108.1, J101.2, U102.1 (VCC), U103.1 (VCC), U104.1 (VCC)
+5V: C104.1, J101.3, L101.2, R101.1, U101.6 (+5VA)
A+: U101.22 (A+), U102.5 (A)
A-: U101.23 (A-), U102.4 (B)
B+: U101.20 (B+), U103.5 (A)
B-: U101.21 (B-), U103.4 (B)
ENC_A: J101.4, U102.3 (RO)
ENC_B: J101.5, U103.3 (RO)
ENC_IW: J101.6, U104.3 (RO)
GND: C101.1, C102.1, C104.2, C105.1, C106.2, C107.2, C108.2, J101.1, R103.2, U101.8 (GND), U101.18 (GND), U102.2 (GND), U103.2 (GND), U104.2 (GND)
IW+: U101.24 (IW+), U104.5 (A)
IW-: U101.1 (IW-), U104.4 (B)
unnamed: C103.2, D101.2 (A), U101.10 (CA)
unnamed: C103.1, D101.1 (K), R101.2, U101.13 (AN)
unnamed: R102.2, TP101.1
unnamed: C105.2, L101.1, U101.19 (+5VD)
unnamed: R103.1, U101.5 (CP+)
unnamed: C101.2, U101.11 (DC1)
unnamed: C102.2, U101.9 (DC2)
unnamed: R102.1, U101.14 (S+)

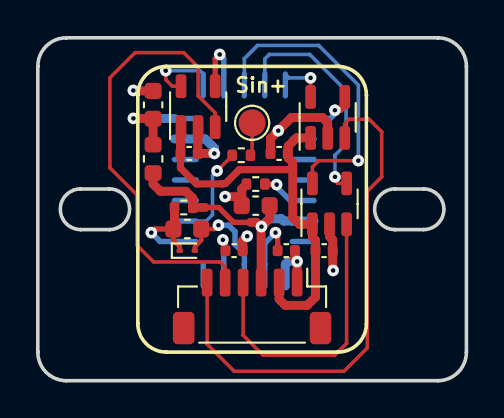
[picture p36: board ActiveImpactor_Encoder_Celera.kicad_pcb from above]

Board: 4 copper layers, 23.8 x 19.1 mm, 19 parts (1 on the bottom side), 20 nets.

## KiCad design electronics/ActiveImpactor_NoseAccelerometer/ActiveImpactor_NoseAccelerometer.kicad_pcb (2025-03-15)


Board: 2 copper layers, 36.5 x 36.5 mm, 13 parts (0 on the bottom side), 7 nets.

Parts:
C101, C102: 100n; C_0402_1005Metric
CLK: CLK; TestPoint_Pad_D1.0mm
CS: CS; TestPoint_Pad_D1.0mm
H101, H102, H103, H104: MountingHole; MountingHole_2.2mm_M2_Pad
INT1: INT1; TestPoint_Pad_D1.0mm
J101: EXP; JST_SH_SM07B-SRSS-TB_1x07-1MP_P1.00mm_Horizontal
MISO: MISO; TestPoint_Pad_D1.0mm
MOSI: MOSI; TestPoint_Pad_D1.0mm
U101: LSM6DS3TR-C; LGA-14_3x2.5mm_P0.5mm_LayoutBorder3x4y

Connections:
+3.3V: C101.1, C102.1, J101.2, U101.5 (VDDIO), U101.8 (VDD)
/CLK: CLK.1, J101.6, U101.13 (SCL)
/CS: CS.1, J101.7, U101.12 (CS)
/INT: INT1.1, J101.3, U101.4 (INT1)
/MISO: J101.5, MISO.1, U101.1 (SDO/SA0)
/MOSI: J101.4, MOSI.1, U101.14 (SDA)
GND: C101.2, C102.2, J101.1, U101.6 (GND), U101.7 (GND)

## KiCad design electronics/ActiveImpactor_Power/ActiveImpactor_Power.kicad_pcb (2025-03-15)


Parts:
C101: 100u; CP_Elec_6.3x5.8; LCSC C128464
C102, C103: 4.7u; C_1206_3216Metric; LCSC C29823
C104: 10n; C_0603_1608Metric; LCSC C57112
C105: 220u; CP_EIA-7343-40_Kemet-Y; LCSC C242173
C106: 10n; C_0402_1005Metric; LCSC C15195
C107: 4.7n; C_0603_1608Metric; LCSC C53987
C108, C109: 4u7; C_0603_1608Metric; LCSC C19666
D101: B340; D_SMA; LCSC C64982
D102: LED_5V; LED_0603_1608Metric; LCSC C965805
D103: LED_EN; LED_0603_1608Metric; LCSC C2286
D104: LED_3.3V; LED_0603_1608Metric; LCSC C965805
H101, H102, H103, H104: #2-56; MountingHole_2.5mm_Pad
J101: Battery; AMASS_XT30U-M_1x02_P5.0mm_Vertical
J102: Balance; JST_XH_B7B-XH-A_1x07_P2.50mm_Vertical; Digikey 455-B7B-XH-A-ND
J103: Control board power; JST_PH_B2B-PH-SM4-TB_1x02-1MP_P2.00mm_Vertical; Digikey 455-B2B-PH-SM4-TBCT-ND
J104: Balance; JST_SH_SM07B-SRSS-TB_1x07-1MP_P1.00mm_Horizontal; LCSC C160406
J105: Charge; JST_PH_S2B-PH-SM4-TB_1x02-1MP_P2.00mm_Horizontal; LCSC C295747
J106: SPI; JST_SH_BM07B-SRSS-TB_1x07-1MP_P1.00mm_Vertical; Digikey 455-BM07B-SRSS-TBCT-ND
L101: 22u; L_Sunlord_MWSA0603S; LCSC C408453
R101: 47k; R_0402_1005Metric; LCSC C25792
R102, R103: 22; R_0402_1005Metric; LCSC C25092
R104: 10k; R_0603_1608Metric; LCSC C25804
R105: 3.24k; R_0603_1608Metric; LCSC C22994
R106, R107, R110, R112: 1k; R_0603_1608Metric; LCSC C21190
R108: 7k5; R_0402_1005Metric; LCSC C137934
R109, R111: 1k; R_0402_1005Metric; LCSC C11702
SW101: SW_SPDT; SW_500SSP1S1M6QEA; Digikey EG2478-ND
TP101: INT1; TestPoint_Pad_D1.0mm
TP102: INT2; TestPoint_Pad_D1.0mm
TP103: MOSI; TestPoint_Pad_D1.0mm
TP104: MISO; TestPoint_Pad_D1.0mm
TP105: CLK; TestPoint_Pad_D1.0mm
TP106: CS; TestPoint_Pad_D1.0mm
TP107: PH; TestPoint_Pad_D1.0mm
TP108: EN; TestPoint_Pad_D1.0mm
TP109: PWM1; TestPoint_Pad_D1.0mm
TP110: PWM2; TestPoint_Pad_D1.0mm
TP111: CUR; TestPoint_Pad_D1.0mm
TP112: +5V; TestPoint_Pad_D1.0mm
TP113: +3.3V; TestPoint_Pad_D1.0mm
U101: TPS5430DDA; TI_SO-PowerPAD-8_ThermalVias; LCSC C9864
U102: TLV70033_SOT23-5; SOT-23-5; LCSC C11337

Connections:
+3.3V: C109.1, R101.1, R112.1, TP113.1, U102.5 (OUT); also elsewhere on the board
+5V: C105.1, C108.1, J103.2, L101.2, R104.1, R106.1, TP112.1, U102.1 (IN), U102.3 (EN)
+BATT: C101.1, C102.1, C103.1, R108.2, SW101.1 (A), U101.7 (VIN); also elsewhere on the board
/H-Bridge/COIL_EN: R111.1, TP108.1; also elsewhere on the board
/H-Bridge/COIL_PWM1: TP109.1; also elsewhere on the board
/H-Bridge/COIL_PWM2: TP110.1; also elsewhere on the board
/H-Bridge/CURRENT: R110.2; also elsewhere on the board
/Microcontroller/ADC_CURRENT: C107.1, R110.1, TP111.1; also elsewhere on the board
/Microcontroller/ADC_VBAT: C106.1, R108.1, R109.2; also elsewhere on the board
/Microcontroller/CLK: J106.6, TP105.1; also elsewhere on the board
/Microcontroller/CS: J106.7, R101.2, TP106.1; also elsewhere on the board
/Microcontroller/INT1: R103.2; also elsewhere on the board
/Microcontroller/INT2: R102.2; also elsewhere on the board
/Microcontroller/MISO: J106.5, TP104.1; also elsewhere on the board
/Microcontroller/MOSI: J106.4, TP103.1; also elsewhere on the board
GND: C101.2, C102.2, C103.2, C105.2, C106.2, C107.2, C108.2, C109.2, D101.2 (A), D102.1 (K), D103.1 (K), D104.1 (K), H101.1, H102.1, H103.1, H104.1, J101.1, J103.1, J105.1, J106.1, R105.2, R109.1, U101.6 (GND), U101.9 (GNDPAD), U102.2 (GND); also elsewhere on the board
unnamed: C104.2, D101.1 (K), L101.1, TP107.1, U101.8 (PH)
unnamed: D102.2 (A), R107.2
unnamed: D103.2 (A), R111.2
unnamed: D104.2 (A), R112.2
unnamed: J101.2, SW101.2 (B)
unnamed: J102.1, J104.1
unnamed: J102.2, J104.2
unnamed: J102.3, J104.3
unnamed: J102.4, J104.4
unnamed: J102.5, J104.5
unnamed: J102.6, J104.6
unnamed: J102.7, J104.7
unnamed: J105.2, SW101.3 (C)
unnamed: J106.2, R103.1, TP101.1
unnamed: J106.3, R102.1, TP102.1
unnamed: R106.2, R107.1
unnamed: C104.1, U101.1 (BOOT)
unnamed: R104.2, R105.1, U101.4 (VSENSE)

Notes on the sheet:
Balance connector
VBAT = 6 * 4.2 = 25.2 V; ADC_VBAT = 2.96
Battery input
Mounting holes
Switching converter
32 kHz cutoff
Control power ouput
add buffer in future revision if necessary
max junction temp 150 C max power = (150 C - 25 C) / (236 C/W) = 0.53 W max current = (0.53 W) / (5 V - 3.3 V) = 429 mA
float EN to enable
3.3V regulator
Provides access to balance connector without removing battery


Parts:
C201: 10u; C_0603_1608Metric; LCSC C19702
C202, C205, C206, C207, C208, C212: 100n; C_0402_1005Metric; LCSC C1525
C203, C204: 2u2; C_0603_1608Metric; LCSC C23630
C209: 1u; C_0402_1005Metric; LCSC C52923
C210: 10n; C_0402_1005Metric; LCSC C15195
C211, C213: 12p; C_0402_1005Metric; LCSC C1547
D201: STAT; LED_0603_1608Metric; LCSC C84266
J201: TagConnect_TC2030-NL; Tag-Connect_TC2030-IDC-NL_2x03_P1.27mm_Vertical
JP201: BOOT0; SolderJumper-2_P1.3mm_Open_RoundedPad1.0x1.5mm
L201: 39n; L_0402_1005Metric; LCSC C26443
R201: 1k; R_0402_1005Metric; LCSC C11702
R202, R203: 10k; R_0402_1005Metric; LCSC C25744
R204: 47; R_0402_1005Metric; LCSC C25118
R205, R206, R207: 22; R_0402_1005Metric; LCSC C25092
SW201: BUTTON; SW_Push_SPST_NO_Alps_SKRK; LCSC C202388
U201: STM32F405RGT6; LQFP-64_10x10mm_P0.5mm; LCSC C15742
Y201: 16MHz; Crystal_SMD_3225-4Pin_3.2x2.5mm; LCSC C13738

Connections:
+3.3V: C201.1, C202.1, C205.1, C206.1, C207.1, C208.1, J201.1 (VCC), JP201.2 (B), L201.1, SW201.2, U201.1 (VBAT), U201.19 (VDD), U201.32 (VDD), U201.48 (VDD), U201.64 (VDD); also elsewhere on the board
+3.3VA: C209.1, C210.1, L201.2, U201.13 (VDDA)
/H-Bridge/COIL_EN: U201.24 (PC4); also elsewhere on the board
/H-Bridge/COIL_PWM1: U201.23 (PA7); also elsewhere on the board
/H-Bridge/COIL_PWM2: U201.41 (PA8); also elsewhere on the board
/Microcontroller/ADC_CURRENT: U201.27 (PB1); also elsewhere on the board
/Microcontroller/ADC_VBAT: U201.26 (PB0); also elsewhere on the board
/Microcontroller/BOOT0: JP201.1 (A), R203.1, U201.60 (BOOT0)
/Microcontroller/BUTTON: R202.1, SW201.1, U201.50 (PA15)
/Microcontroller/CLK: U201.34 (PB13); also elsewhere on the board
/Microcontroller/CS: U201.33 (PB12); also elsewhere on the board
/Microcontroller/HSE_IN: C211.1, U201.5 (PH0), Y201.1
/Microcontroller/HSE_OUT: R204.1, U201.6 (PH1)
/Microcontroller/INT1: U201.37 (PC6); also elsewhere on the board
/Microcontroller/INT2: U201.38 (PC7); also elsewhere on the board
/Microcontroller/LED_STATUS: D201.2 (A), U201.51 (PC10)
/Microcontroller/MISO: U201.35 (PB14); also elsewhere on the board
/Microcontroller/MOSI: U201.36 (PB15); also elsewhere on the board
/Microcontroller/SWD_NRST: C212.1, J201.3 (~RESET), U201.7 (NRST)
/Microcontroller/SWD_SWCLK: R205.1, U201.49 (PA14)
/Microcontroller/SWD_SWDIO: R206.1, U201.46 (PA13)
/Microcontroller/SWD_SWO: R207.1, U201.55 (PB3)
GND: C201.2, C202.2, C203.2, C204.2, C205.2, C206.2, C207.2, C208.2, C209.2, C210.2, C211.2, C212.2, C213.2, J201.5 (GND), R201.2, R202.2, R203.2, U201.12 (VSSA), U201.18 (VSS), U201.63 (VSS), Y201.2, Y201.4; also elsewhere on the board
unnamed: C213.1, R204.2, Y201.3
unnamed: D201.1 (K), R201.1
unnamed: J201.4 (SWCLK), R205.2
unnamed: J201.2 (SWDIO), R206.2
unnamed: J201.6 (SWO), R207.2
unnamed: C203.1, U201.31 (VCAP_1)
unnamed: C204.1, U201.47 (VCAP_2)

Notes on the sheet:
C_load = 2 * (C_load,crystal - C_stray) = 2 * (12 pf - ~6 pf)
Debug header
Leave in run mode and program with SWD. Solder jumper option to set boot mode
User button
One 100n decoupling cap per VDD pin, close to pin
Low ESR
Boot mode
Status LED
Extra filtering for analog supply
Capacitor to prevent spurious resets
Run mode
10u bulk decoupling, close to microcontroller
External crystal oscillator (refer to AN2867 by ST)
Coil PWM on TIM1_CH1 and TIM1_CH1N Using SPI2 for communication Current sense uses ADC1_IN9 Battery voltage sense with ADC2_IN8
Series resistors reduce ringing in high speed lines, place at driving end
Resistor prevents overdriving crystal (noise)


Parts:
C301: 330n; C_0603_1608Metric; LCSC C188679
C302, C309: 470n; C_0402_1005Metric; LCSC C437527
C303, C305: 100n; C_0603_1608Metric; LCSC C14663
C304, C308: 47n; C_0402_1005Metric; LCSC C880605
C306, C307: 1u; C_1206_3216Metric; LCSC C1848
D301, D304, D305, D306, D307, D310: 1N5819; D_SOD-523; LCSC C5451630
D302, D303, D308, D309: 1N4148WT; D_SOD-523; LCSC C727112
J301: Coil; JST_PH_S2B-PH-SM4-TB_1x02-1MP_P2.00mm_Horizontal; LCSC C295747
Q301, Q302, Q303, Q304: SIR182DP; PowerPAK_SO-8_Single; LCSC C467943
R301, R307: 20k; R_0402_1005Metric; LCSC C25765
R302: 6m; R_2512_6332Metric; LCSC C2985709
R303, R304, R305, R306: 10; R_0402_1005Metric; LCSC C25077
TP301: +12V; TestPoint_Pad_D1.0mm
U301: L7812; TO-252-2; LCSC C16424
U302, U304: LM5106; VSSOP-10_3x3mm_P0.5mm; LCSC C91879
U303: INA240A2PWR; TSSOP-8_4.4x3mm_P0.65mm; LCSC C129949

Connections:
+3.3V: C305.1, U303.5 (V+), U303.6 (REF2); also elsewhere on the board
+12V: C302.1, C303.1, C309.1, D301.2 (A), D310.2 (A), TP301.1, U301.3 (OUT), U302.1 (VDD), U304.1 (VDD)
+BATT: C301.1, C306.1, C307.1, D304.1 (K), D306.1 (K), Q301.5 (D), Q303.5 (D), U301.1 (IN); also elsewhere on the board
/H-Bridge/BRIDGE1: C304.2, D304.2 (A), D305.1 (K), Q301.1 (S), Q301.2 (S), Q301.3 (S), Q302.5 (D), R302.1, U302.4 (HS), U303.2 (+)
/H-Bridge/BRIDGE2: C308.2, D306.2 (A), D307.1 (K), J301.2, Q303.1 (S), Q303.2 (S), Q303.3 (S), Q304.5 (D), U304.4 (HS)
/H-Bridge/COIL_EN: U302.7 (EN), U304.7 (EN); also elsewhere on the board
/H-Bridge/COIL_PWM1: U302.8 (IN); also elsewhere on the board
/H-Bridge/COIL_PWM2: U304.8 (IN); also elsewhere on the board
/H-Bridge/CURRENT: U303.8; also elsewhere on the board
GND: C301.2, C302.2, C303.2, C305.2, C306.2, C307.2, C309.2, D305.2 (A), D307.2 (A), Q302.1 (S), Q302.2 (S), Q302.3 (S), Q304.1 (S), Q304.2 (S), Q304.3 (S), R301.1, R307.1, U301.2 (GND), U302.9 (VSS), U303.1 (GND), U303.4 (GND), U303.7 (REF1), U304.9 (VSS); also elsewhere on the board
unnamed: C304.1, D301.1 (K), U302.2 (HB)
unnamed: D302.2 (A), Q301.4 (G), R303.2
unnamed: D302.1 (K), R303.1, U302.3 (HO)
unnamed: D303.2 (A), Q302.4 (G), R304.2
unnamed: D303.1 (K), R304.1, U302.10 (LO)
unnamed: D308.2 (A), Q303.4 (G), R305.2
unnamed: D308.1 (K), R305.1, U304.3 (HO)
unnamed: D309.2 (A), Q304.4 (G), R306.2
unnamed: D309.1 (K), R306.1, U304.10 (LO)
unnamed: C308.1, D310.1 (K), U304.2 (HB)
unnamed: J301.1, R302.2, U303.3 (-)
unnamed: R301.2, U302.6 (RDT)
unnamed: R307.2, U304.6 (RDT)

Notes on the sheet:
H-bridge
C_BYPASS = 10 * C_BOOT = 470 nF
gate drivers only draw (average) 3.5 mA max
V_HB = V_DD - V_DH - V_HBL = 12 V - 0.6 V - 6.9 V = 4.5 V
12V regulator
RDT = 20k for 150 ns of dead time
C_BOOT = 35 nC / 4.5 V = 7 nF -> pick 47 nF for headroom
P_SENSE = I_COIL^2 R_RENSE = (5.73 A)^2 (0.006 ohm) = 197 mW
V_SENSE = I_COIL R_SENSE gain = (+/-5.73 A) (0.006 ohm) (50) = +/- 1.72 V
I_COIL = V_BAT / R_COIL = 25.2 V / 4.4 ohm = 5.73 A
Current sense and coil connector



Board: 4 copper layers, 33.3 x 93.7 mm, 115 parts (18 on the bottom side), 67 nets.

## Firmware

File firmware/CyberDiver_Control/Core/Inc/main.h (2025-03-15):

/* USER CODE BEGIN Header */
/**
  ******************************************************************************
  * @file           : main.h
  * @brief          : Header for main.c file.
  *                   This file contains the common defines of the application.
  ******************************************************************************
  * @attention
  *
  * Copyright (c) 2024 STMicroelectronics.
  * All rights reserved.
  *
  * This software is licensed under terms that can be found in the LICENSE file
  * in the root directory of this software component.
  * If no LICENSE file comes with this software, it is provided AS-IS.
  *
  ******************************************************************************
  */
/* USER CODE END Header */

/* Define to prevent recursive inclusion -------------------------------------*/
#ifndef __MAIN_H
#define __MAIN_H

#ifdef __cplusplus
extern "C" {
#endif

/* Includes ------------------------------------------------------------------*/
#include "stm32h7xx_hal.h"

/* Private includes ----------------------------------------------------------*/
/* USER CODE BEGIN Includes */

/* USER CODE END Includes */

/* Exported types ------------------------------------------------------------*/
/* USER CODE BEGIN ET */

/* USER CODE END ET */

/* Exported constants --------------------------------------------------------*/
/* USER CODE BEGIN EC */

/* USER CODE END EC */

/* Exported macro ------------------------------------------------------------*/
/* USER CODE BEGIN EM */

/* USER CODE END EM */

/* Exported functions prototypes ---------------------------------------------*/
void Error_Handler(void);

/* USER CODE BEGIN EFP */

/* USER CODE END EFP */

/* Private defines -----------------------------------------------------------*/
#define EXP_INT_Pin GPIO_PIN_3
#define EXP_INT_GPIO_Port GPIOE
#define LED_STATUS_Pin GPIO_PIN_14
#define LED_STATUS_GPIO_Port GPIOC
#define BUTTON_Pin GPIO_PIN_15
#define BUTTON_GPIO_Port GPIOC
#define ENC_IW_Pin GPIO_PIN_2
#define ENC_IW_GPIO_Port GPIOA
#define SPI6_NSS_Pin GPIO_PIN_4
#define SPI6_NSS_GPIO_Port GPIOA
#define SD_DET_Pin GPIO_PIN_11
#define SD_DET_GPIO_Port GPIOD
#define PWR_INT2_Pin GPIO_PIN_4
#define PWR_INT2_GPIO_Port GPIOD
#define PWR_INT1_Pin GPIO_PIN_5
#define PWR_INT1_GPIO_Port GPIOD
#define SPI1_NSS_Pin GPIO_PIN_10
#define SPI1_NSS_GPIO_Port GPIOG
#define IIS3DWB_INT1_Pin GPIO_PIN_4
#define IIS3DWB_INT1_GPIO_Port GPIOB
#define IIS3DWB_INT1_EXTI_IRQn EXTI4_IRQn
#define IIS3DWB_INT2_Pin GPIO_PIN_5
#define IIS3DWB_INT2_GPIO_Port GPIOB
#define ADXL372_INT1_Pin GPIO_PIN_6
#define ADXL372_INT1_GPIO_Port GPIOB
#define ADXL372_INT2_Pin GPIO_PIN_7
#define ADXL372_INT2_GPIO_Port GPIOB
#define LSM6DS3_INT1_Pin GPIO_PIN_8
#define LSM6DS3_INT1_GPIO_Port GPIOB
#define LSM6DS3_INT2_Pin GPIO_PIN_9
#define LSM6DS3_INT2_GPIO_Port GPIOB

/* USER CODE BEGIN Private defines */

/* USER CODE END Private defines */

#ifdef __cplusplus
}
#endif

#endif /* __MAIN_H */

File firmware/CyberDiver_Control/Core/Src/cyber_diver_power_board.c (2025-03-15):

/*
 * cyber_diver_power_board.c
 *
 *  Created on: Jul 10, 2024
 *      Author: johnt
 */

#include "cyber_diver_power_board.h"
#include "fast_spi.h"

void CyberDiverPowerBoard_Init(CyberDiverPowerBoard* power_board,
		CyberDiverPowerBoard_Config* config,
		SPI_HandleTypeDef* spi,
		GPIO_TypeDef* cs_port,
		uint16_t cs_pin,
		GPIO_TypeDef* int1_port,
		uint16_t int1_pin,
		GPIO_TypeDef* int2_port,
		uint16_t int2_pin)
{
	power_board->config = config;
	power_board->spi = spi;
	power_board->cs_port = cs_port;
	power_board->cs_pin = cs_pin;

	power_board->int1_port = int1_port;
	power_board->int1_pin = int1_pin;
	power_board->int2_port = int2_port;
	power_board->int2_pin = int2_pin;

	power_board->mode = POWER_BOARD_IDLE;
	power_board->mode_stable = 0;
	HAL_GPIO_WritePin(power_board->int1_port, power_board->int1_pin, POWER_BOARD_IDLE);
	HAL_Delay(1);
	power_board->mode_stable = 1;

}


uint32_t CyberDiverPowerBoard_Reset(CyberDiverPowerBoard* power_board)
{
	power_board->measured_current_amps = 0;
	power_board->measured_duty_cycle = 0;

	/* send the configuration to the power board */
	CyberDiverPowerBoard_SetMode(power_board, POWER_BOARD_IDLE);
	if (!CyberDiverPowerBoard_UpdateConfig(power_board))
		return 0;

	return 1;
}



void CyberDiverPowerBoard_SetMode(CyberDiverPowerBoard* power_board, CyberDiverPowerBoardMode mode)
{
	/* sets the mode of the power board object and updates the INT pin states accordingly */
	if (power_board->mode != mode)
	{
		power_board->mode_stable = 0;
		power_board->mode = mode;
		HAL_Delay(1);  /* make sure we don't try to talk to the power board too close to a mode change */
		HAL_GPIO_WritePin(power_board->int1_port, power_board->int1_pin, mode);
		HAL_Delay(1);
		power_board->mode_stable = 1;
	}

}


CyberDiverPowerBoardMode CyberDiverPowerBoard_GetMode(CyberDiverPowerBoard* power_board)
{
	return power_board->mode;
}


void CyberDiverPowerBoard_SetCurrent(CyberDiverPowerBoard* power_board, float setpoint_current_amps, float measured_velocity_mmps)
{
	if (power_board->mode == POWER_BOARD_RUNNING && power_board->mode_stable)
	{
		/* store the new command data in the power board object */
		if (setpoint_current_amps >= 5.5) setpoint_current_amps = 5.5;
		if (setpoint_current_amps <= -5.5) setpoint_current_amps = -5.5;
		power_board->tx_data.setpoint_current_scaled = (int16_t)(setpoint_current_amps * CD_PB_CURRENT_SCALE);
		power_board->tx_data.measured_velocity_scaled = (int16_t)(measured_velocity_mmps * CD_PB_VEL_SCALE);

		/* do the SPI communication with our fast implementation */
		SPI_TxRx_Fast((uint8_t*)&(power_board->tx_data), (uint8_t*)&(power_board->rx_data), 4,
				power_board->spi->Instance, power_board->cs_port, power_board->cs_pin);

		/* store the data we got back from the power board */
		power_board->measured_current_amps = (float)power_board->rx_data.measured_current_scaled / CD_PB_CURRENT_SCALE;
		power_board->measured_duty_cycle = (float)power_board->rx_data.measured_duty_cycle_scaled / CD_PB_DUTY_SCALE;
	}
}


float CyberDiverPowerBoard_GetCurrent(CyberDiverPowerBoard* power_board)
{
	return power_board->measured_current_amps;
}


float CyberDiverPowerBoard_GetDutyCycle(CyberDiverPowerBoard* power_board)
{
	return power_board->measured_duty_cycle;
}


uint32_t CyberDiverPowerBoard_SetGains(CyberDiverPowerBoard* power_board, float Kp, float Ki, float Kd, float Kff)
{

	float Kp_old = power_board->config->cur_pid_config.Kp;
	float Ki_old = power_board->config->cur_pid_config.Ki;
	float Kd_old = power_board->config->cur_pid_config.Kd;
	float Kff_old = power_board->config->cur_pid_config.Kff;

	power_board->config->cur_pid_config.Kp = Kp;
	power_board->config->cur_pid_config.Ki = Ki;
	power_board->config->cur_pid_config.Kd = Kd;
	power_board->config->cur_pid_config.Kff = Kff;

	if (CyberDiverPowerBoard_UpdateConfig(power_board))
	{
		return 1;
	}
	else
	{
		/* revert the settings */
		power_board->config->cur_pid_config.Kp = Kp_old;
		power_board->config->cur_pid_config.Ki = Ki_old;
		power_board->config->cur_pid_config.Kd = Kd_old;
		power_board->config->cur_pid_config.Kff = Kff_old;
	}

	return 0;
}


void CyberDiverPowerBoard_GetGains(CyberDiverPowerBoard* power_board, float* Kp, float* Ki, float* Kd, float* Kff)
{
	*Kp = power_board->config->cur_pid_config.Kp;
	*Ki = power_board->config->cur_pid_config.Ki;
	*Kd = power_board->config->cur_pid_config.Kd;
	*Kff = power_board->config->cur_pid_config.Kff;
}


uint32_t CyberDiverPowerBoard_SetPeriod(CyberDiverPowerBoard* power_board, float T)
{
	/* inner control loop update period */
	/* WARNING: this should only be updated with scope connected to verify that the CPU can keep up */

	float T_old = power_board->config->cur_pid_config.T;

	uint32_t arr = CD_PB_TIM_COUNTS_PER_SECOND / (1.0f / T) / 2;
	power_board->config->cur_pid_config.T = (float)(2.0f * arr) / (float)(CD_PB_TIM_COUNTS_PER_SECOND);  /* update the value in the configuration so that it divides evenly into the timer frequency */

	if (CyberDiverPowerBoard_UpdateConfig(power_board))
	{
		return 1;
	}
	else
	{
		/* revert the settings */
		power_board->config->cur_pid_config.T = T_old;
	}


	return 0;
}


float CyberDiverPowerBoard_GetPeriod(CyberDiverPowerBoard* power_board)
{
	return power_board->config->cur_pid_config.T;
}


uint32_t CyberDiverPowerBoard_SetTau(CyberDiverPowerBoard* power_board, float tau)
{
	if (tau > 0)
	{
		float tau_old = power_board->config->cur_pid_config.tau;
		power_board->config->cur_pid_config.tau = tau;
		if (CyberDiverPowerBoard_UpdateConfig(power_board))
		{
			return 1;
		}
		else
		{
			/* revert the settings */
			power_board->config->cur_pid_config.tau = tau_old;
		}
	}

	return 0;
}


float CyberDiverPowerBoard_GetTau(CyberDiverPowerBoard* power_board)
{
	return power_board->config->cur_pid_config.tau;
}


uint32_t CyberDiverPowerBoard_SetKffvel(CyberDiverPowerBoard* power_board, float Kff_vel)
{
	float Kff_vel_old = power_board->config->Kff_vel;

	power_board->config->Kff_vel = Kff_vel;

	if (CyberDiverPowerBoard_UpdateConfig(power_board))
	{
		return 1;
	}
	else
	{
		/* revert the settings */
		power_board->config->Kff_vel = Kff_vel_old;
	}

	return 0;
}


float CyberDiverPowerBoard_GetKffvel(CyberDiverPowerBoard* power_board)
{
	return power_board->config->Kff_vel;
}


uint32_t CyberDiverPowerBoard_UpdateConfig(CyberDiverPowerBoard* power_board)
{
	/* send the most recent configuration to the power board */

	if (power_board->mode == POWER_BOARD_IDLE && power_board->mode_stable)
	{
		uint8_t rx_buf[sizeof(CyberDiverPowerBoard_Config)] = {0};  /* empty rx buffer */
		HAL_GPIO_WritePin(power_board->cs_port, power_board->cs_pin, GPIO_PIN_RESET);
		uint32_t ret = (HAL_OK == HAL_SPI_TransmitReceive(power_board->spi, (uint8_t*)(power_board->config), rx_buf, sizeof(CyberDiverPowerBoard_Config), HAL_MAX_DELAY));  /* just send the whole configuration object */
		HAL_GPIO_WritePin(power_board->cs_port, power_board->cs_pin, GPIO_PIN_SET);

		if (ret && !strcmp((char*)rx_buf, CD_PB_CONFIG_VALIDATION))  /* check that we successfully talked to the power board, rx_buf should contain the validation string */
			return 1;
	}

	return 0;
}

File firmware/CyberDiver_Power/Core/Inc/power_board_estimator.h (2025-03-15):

/*
 * power_board_estimator.h
 *
 *  Created on: Sep 11, 2024
 *      Author: johnt
 */

#ifndef INC_POWER_BOARD_ESTIMATOR_H_
#define INC_POWER_BOARD_ESTIMATOR_H_

#include <stdint.h>
#include <math.h>

/* responsible for estimating the system state (true coil current) based on the ADC measurements */

#define PB_NUM_SAMPLES_PER_CYCLE 4  /* we sample 4 types per period in the SVPWM-style H-bridge modulation, and the samples should all be the mean current value at steady state */
#define PB_ADC_MAX_READING 4095.0f
#define PB_ADC_MAX_VOLTAGE 3.3f
#define PB_R_SENSE 0.006f
#define PB_CUR_AMP_GAIN 50.0f
#define PB_AMPS_PER_BIT PB_ADC_MAX_VOLTAGE / (PB_ADC_MAX_READING * PB_R_SENSE * PB_CUR_AMP_GAIN)

#define PB_SAMPLE_DISCARD_THRESHOLD 0.25f


typedef struct
{

} PowerBoardEstimator_Config;

typedef struct
{
	PowerBoardEstimator_Config* config;

	uint16_t adc_current[2 * PB_NUM_SAMPLES_PER_CYCLE];
	volatile uint32_t adc_buf_offset;  /* offset index for double buffering the ADC readings */

	/*
	 * Each cycle, we want to keep track of when the MOSFET switching occurs so we can reject samples that fall too close to an edge (common mode ringing corrupts the sample)
	 * This array contains flags of whether to use or discard each sample
	 */
	uint8_t use_sample[4];
	volatile uint32_t samples_available;


} PowerBoardEstimator;

void PowerBoardEstimator_Init(PowerBoardEstimator* estimator);
void PowerBoardEstimator_Reset(PowerBoardEstimator* estimator);

float PowerBoardEstimator_GetCurrent(PowerBoardEstimator* estimator);
void PowerBoardEstimator_SetDuty(PowerBoardEstimator* estimator, float duty_cycle);  /* tell the estimator the duty cycle for the next period so it can elect to ignore samples too close to edges */

uint32_t PowerBoardEstimator_GetIndividualSamples(PowerBoardEstimator* estimator, uint16_t* samples);  /* for calibration, returns true if new samples are available and then passes them through the argument */

#endif /* INC_POWER_BOARD_ESTIMATOR_H_ */

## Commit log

2025-03-15 added board designs
    [ActiveImpactor_Control-CuBottom.gbr, ActiveImpactor_Control-CuIn1.gbr, ActiveImpactor_Control-CuIn2.gbr, ActiveImpactor_Control-CuTop.gbr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]
2025-03-16 added schematics and flexure scripts
    [SDRAM.kicad_sch]
2025-03-16 added assets and raw data files
    [static_force_test_10n_threshold.csv, static_force_test_15n_threshold.csv, static_force_test_15npmm.csv, static_force_test_20n_threshold.csv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]
2025-03-16 added csvs with aggregate data
    [linear damped.csv, linear undamped.csv, nonlinear.csv]
2025-03-16 added matlab scripts
    [shiffman_spencer_sphere_dmdx.csv]
